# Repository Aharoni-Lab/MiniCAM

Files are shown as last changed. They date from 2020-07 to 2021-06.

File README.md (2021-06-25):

# MiniCAM
The MiniCAM is an open-source behaviroal camera for imaging freely behaving animals in behavioral and neuroscience experiments. The goal of the MiniCAM project is to provide an open-source, customizable, high-quality, and affordable alternative to using webcams or scientific USB cameras for behavioral imaging. The MiniCAM is powered and communicates over any commercial 50ohm coaxial cable minimizing the cabling that needs to run into the experimental environment. The coaxial cable connects the MiniDAQ to any version of UCLA Miniscope DAQs or MiniDAQs which then connects over USB3 to a host computer.

Using the [Miniscope Software](https://github.com/Aharoni-Lab/Miniscope-DAQ-QT-Software), multiple Miniscopes and MiniCAMs can be connected, streamed, and time-sync'ed recording simultaniously.

<p align="center">
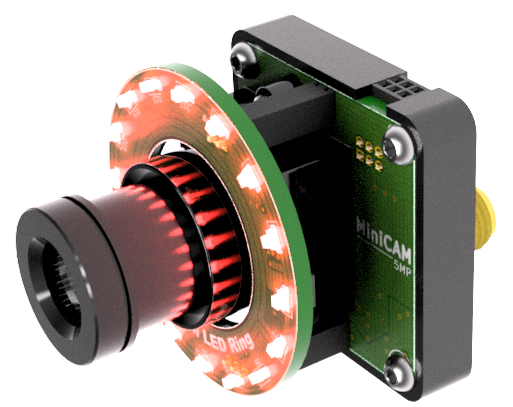
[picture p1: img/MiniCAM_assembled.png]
  
</p>

## MiniCAM Components
The MiniCAM consists of a custom printed circuit board (PCB), a 3D printed housing, an off the shelf M12 lens mount, a M12 camera lens, and an optional LED illumination ring. The PCB contains a 5MP CMOS image sensor, support electronics to power and serialize the imaging data, and an SMA coax connector. The image sensor can be configured through the Miniscope software and the optional LED illumination ring intensity can also be controlled through software. The MiniCAM runs at 50fps with 1024X768 resolution as the default configuration. Higher frame rate can be achieved by choosing smaller resolutions and higher resolution comes with lower frame rate.

<p align="center">
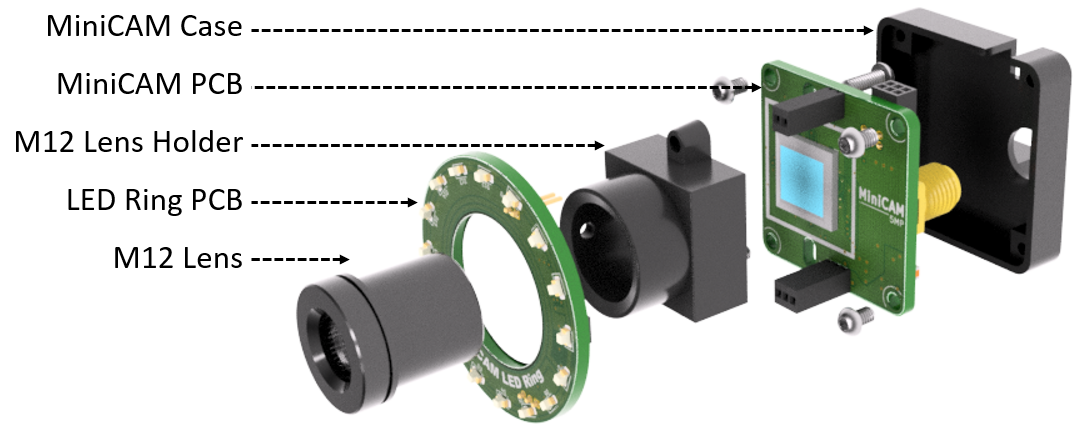
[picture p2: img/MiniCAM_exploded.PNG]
  
</p>

## System Layout
The MiniCAM requires a UCLA Miniscope Data Acquisition (DAQ) board (connected over a 50ohm coaxial cable) and a host computer (connected over USB3) running the [Miniscope Software](https://github.com/Aharoni-Lab/Miniscope-DAQ-QT-Software) (or other third-party application that can stream UVC cameras and can communicate through a Miniscope DAQ). You can use any generation of Miniscope DAQ but you must update it with [the newest firmware](https://github.com/Aharoni-Lab/Miniscope-DAQ-Cypress-firmware). You can also use the cheaper and smaller version of the Miniscope DAQ called the MiniDAQ (open-source link coming soon). Once updated to the newest firmware, any Miniscope DAQ device will work with all Miniscope and MiniCAM devices. 

<p align="center">
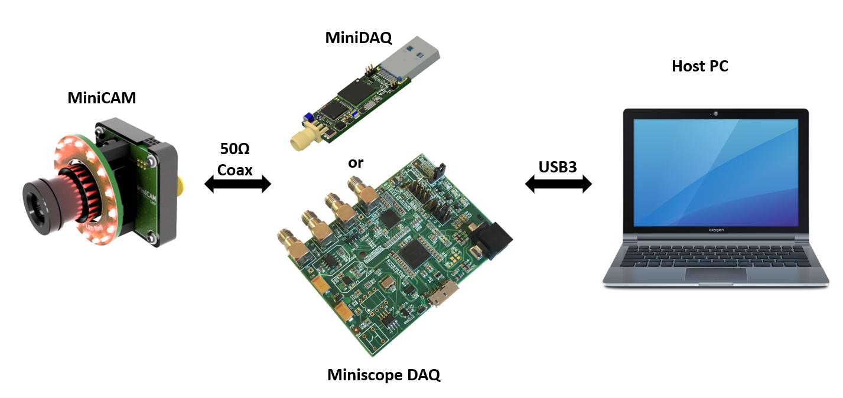
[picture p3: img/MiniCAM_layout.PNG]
  
</p>

## M12 lenses and Coaxial Cables
Just like Miniscopes, the MiniCAM uses a 50Ohm coaxial cable for power, communication, and data. Any 50Ohm coax cable should work with the system. 

### M12 lenses
M12 lenses and M12 Mount Lens Holders are avaiable in Amazon (can be purchased at other places too). It can be handy to buy a M12 Lens Kit that comes with a range of M12 lenses for different view angles. We have been happy with the Arducam lens set which can be found on Amazon. If you are using the optional LED illumination ring or other nIR light source make sure to remove any IR filter located in the lens if applicable.

### Coaxial Cables
Any 50Ohm coaxial cable should be compatible with this system. It is not necessary to use the expensive, thin, flexible coax cables generally used with Miniscopes. The thicker the cable the longer length you can run (maxing out at around 10 to 15 meters). It generally is most convinient to get a coax cable with male SMA connectors on both ends to connect between the MiniCAM and MiniDAQ (or standard Miniscope DAQ).

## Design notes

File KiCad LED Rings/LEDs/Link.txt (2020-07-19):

https://www.soselectronic.com/standard-leds?query=kptd&params=9%3ARed%7C121%3A30&param_current=121

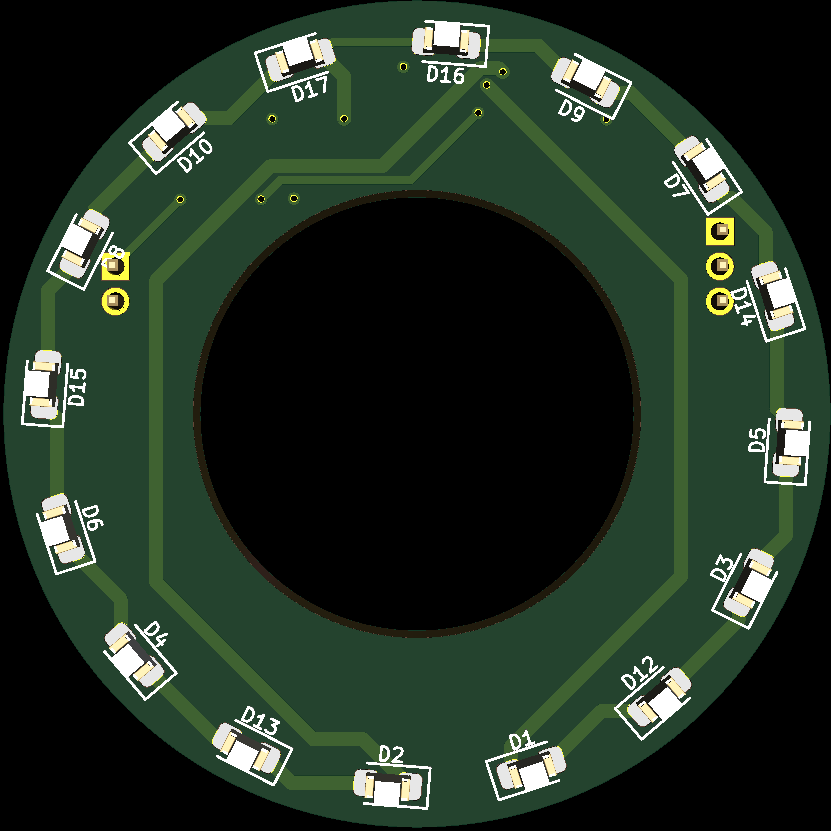
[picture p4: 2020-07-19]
KiCad LED Rings/LED Rings-V2 Skins/Front.PNG

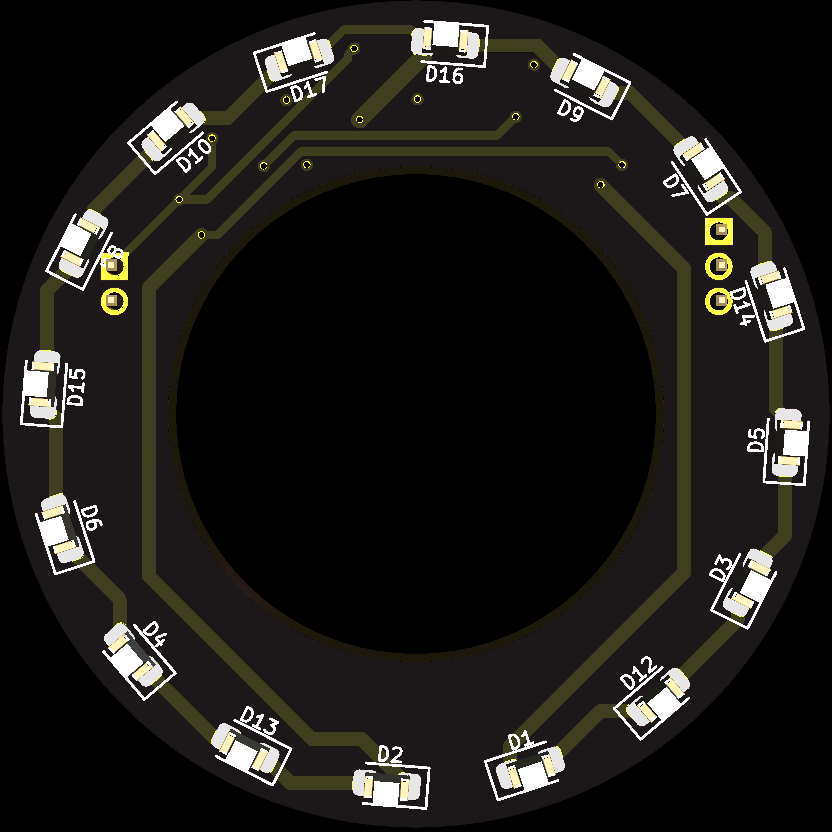
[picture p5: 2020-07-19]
KiCad LED Rings/LED Rings-V2 Skins/Front_b.png

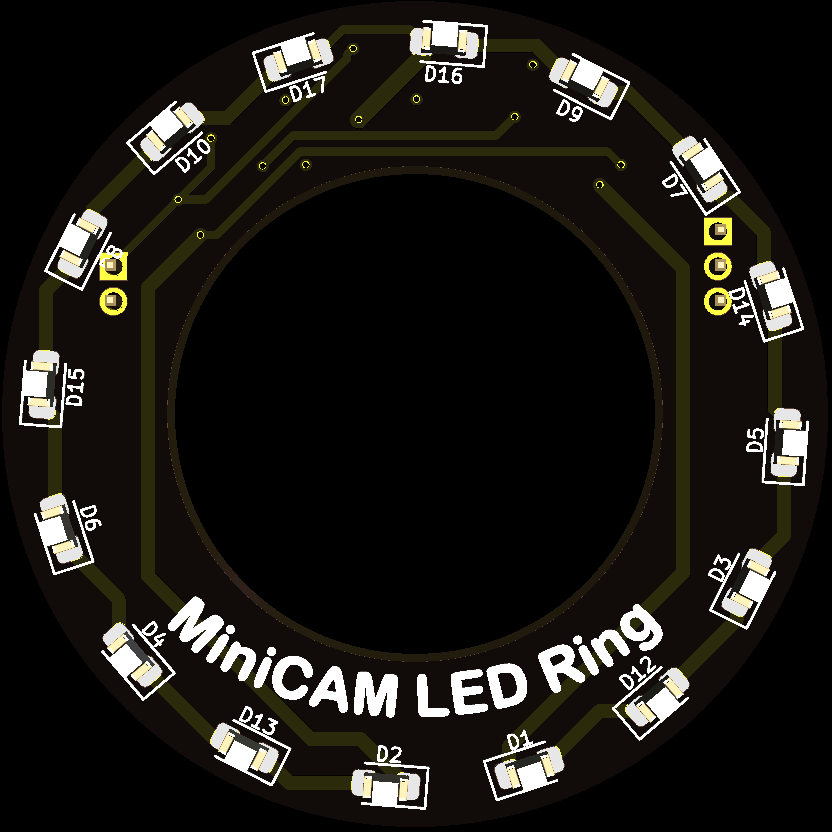
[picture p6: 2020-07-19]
KiCad LED Rings/LED Rings-V2 Skins/Front_b2.png

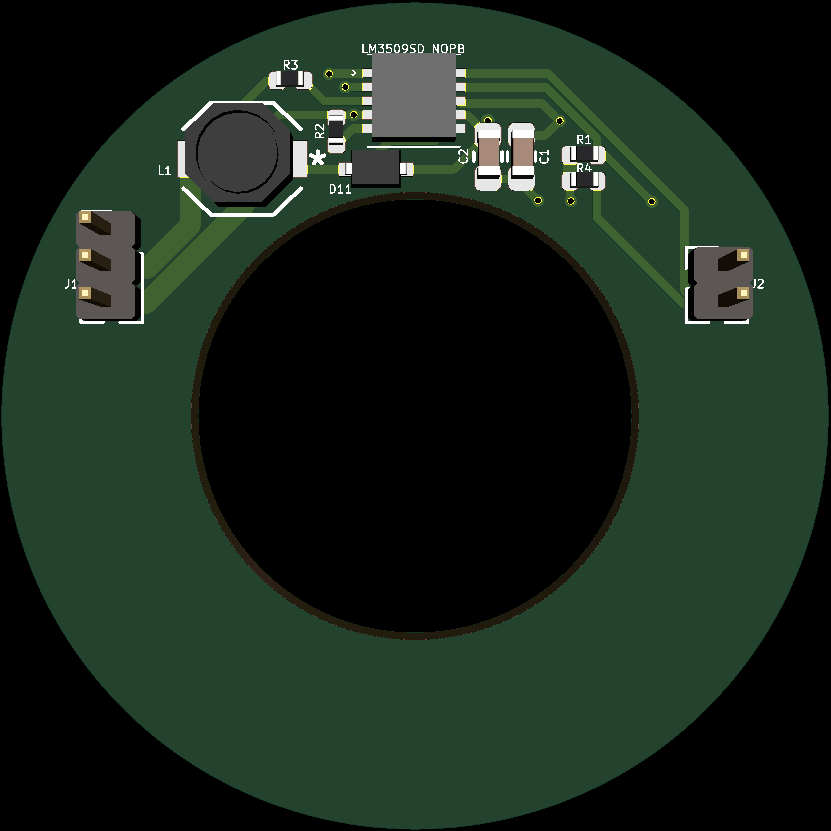
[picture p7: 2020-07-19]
KiCad LED Rings/LED Rings-V2 Skins/Back.PNG

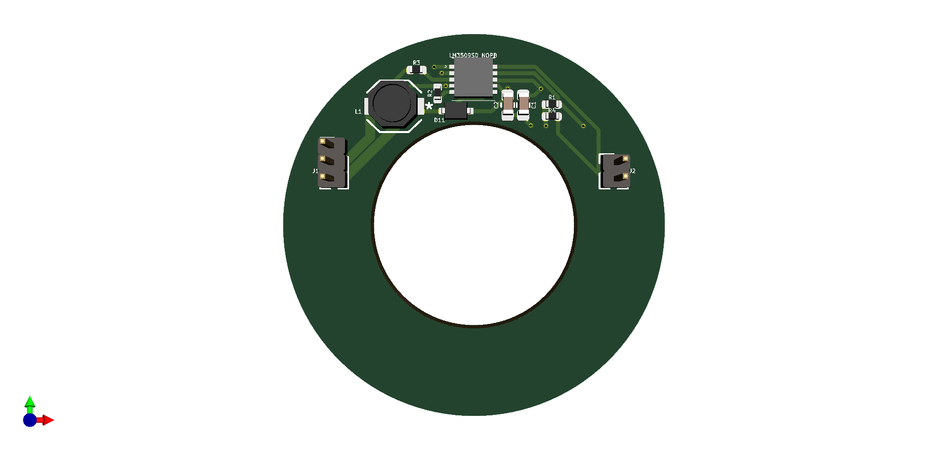
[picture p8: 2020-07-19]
KiCad LED Rings/LED Rings-V2 Skins/Kicad_BehaviorCamera_V2 v5_B.png

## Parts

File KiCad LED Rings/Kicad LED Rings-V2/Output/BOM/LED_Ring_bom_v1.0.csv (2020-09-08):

Component | Description | Part | References | Value | Footprint | Quantity Per PCB | Datasheet | PartNo.
1 |  | GRM033R60J105MEA2D-.Capacitor-Kicad-LED-Rings-rescue-Kicad-LED-Rings-rescue | C1 | 1uF | C_0603_1608Metric_L | 1 | ~ | GRT188R61C105KE13D
2 |  | GRM033R60J105MEA2D-.Capacitor-Kicad-LED-Rings-rescue-Kicad-LED-Rings-rescue | C2 | 2.2uF | C_0805_2012Metric_L | 1 | https://www.digikey.com/product-detail/en/tdk-corporation/C2012X5R1E225M125AC/445-7630-2-ND/2733065 | C2012X5R1E225M125AC
3 |  | BAT760,115-BAT760_115-Kicad-LED-Rings-rescue | D17 | D_Schottky | SOD323(F) | 1 | https://www.digikey.com/product-detail/en/nexperia-usa-inc/BAT760115/1727-4825-1-ND/2531312 | BAT760,115
4 |  | LED_Small_ALT-Device-Kicad-LED-Rings-rescue | D1 D2 D3 D4 D5 D6 D7 D8 D9 D10 D11 D12 D13 D14 D15 D16 | LED_Small_ALT | LED_0603_1608Metric | 16 | https://www.digikey.com/product-detail/en/lite-on-inc/LTST-C190KRKT/160-1436-1-ND/386816 | LTST-C190KRKT
5 |  | Conn_01x03_Female-Connector-Kicad-LED-Rings-rescue | J1 | Conn_01x02_Female | PinHeader_1x03_P1.27mm_Vertical | 1 | ~
6 |  | Conn_01x02_Male-Connector-Kicad-LED-Rings-rescue | J2 | Conn_01x02_Male | PinHeader_1x02_P1.27mm_Vertical | 1 | ~
7 |  | NRS4012T100MDGJ-2020-07-30_23-38-29 | L1 | 10uH | NR3015T1R5N | 1 | https://www.digikey.com/product-detail/en/taiyo-yuden/NRS4012T100MDGJ/587-2878-1-ND/2648998 | NRS4012T100MDGJ
8 |  | R_Small-Device-Kicad-LED-Rings-rescue | R1 R4 | 3K | R_0402_1005Metric_ERJ_L | 2 | https://www.digikey.in/product-detail/en/panasonic-electronic-components/ERA-2AEB302X/P3-0KDCTR-ND/1706016 | ERA-2AEB302X
9 |  | R_Small-Device-Kicad-LED-Rings-rescue | R2 R3 | 9.5k | R_0402_1005Metric_ERJ_L | 2 | https://www.digikey.com/product-detail/en/panasonic-electronic-components/ERA-2AEB123X/P12KDCCT-ND/1706209 | ERA-2AEB9531X
10 |  | LM3509SD_NOPB-2020-04-05_20-57-04-Kicad-LED-Rings-rescue | U1 | LM3509SD_NOPB | LM3509SDNOPB | 1 |  | LM3509SD_NOPB
Component Groups: | 10
Component Count: | 27
Fitted Components: | 27
Number of PCBs: | 1
Total components: | 27
Schematic Version: | v1.0
Schematic Date: | 2020-09-08
PCB Variant: | [u'default']
BoM Date: | 9/8/2020 11:45:49 AM
Schematic Source: | LED_Ring.sch
KiCad Version: | Eeschema (5.1.6)-1

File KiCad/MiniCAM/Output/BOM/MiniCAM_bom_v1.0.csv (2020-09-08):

Component | Description | Part | References | Value | Footprint | Quantity Per PCB | Datasheet | Part Number | Note | Size
1 | Unpolarized capacitor, small symbol | C_Small | C18 C21 C26 C29 C31 C34 | 10nF | C_0402_1005Metric_L | 6 | ~ | GCM155R71E103KA37D
2 | Unpolarized capacitor, small symbol | C_Small | C25 | 47nF | C_0402_1005Metric_L | 1 | ~ | GRM155R71A473KA01D
3 | Unpolarized capacitor, small symbol | C_Small | C4 C5 C6 C7 C8 C9 C10 C14 C15 C19 C22 C24 C27 C30 C32 | 0.1uF | C_0402_1005Metric_L | 15 | ~ | GCM155R71C104KA55J
4 | Unpolarized capacitor, small symbol | C_Small | C1 C2 C3 C11 C16 C33 C35 | 1uF | C_0402_1005Metric_L | 7 | ~ | GRT155R61C105KE01D
5 | Unpolarized capacitor, small symbol | C_Small | C20 C23 C28 | 4.7uF | C_0402_1005Metric_L | 3 | ~ | CC0402MRX5R6BB475
6 | Unpolarized capacitor, small symbol | C_Small | C12 C13 C17 C36 | 10uF | C_0603_1608Metric_L | 4 | ~ | GRM188R61A106KE69J
7 | Light emitting diode, small symbol, filled shape | LED_Small_ALT | D1 | LED_Small_ALT | LED_SC80X160X65L40L | 1 | ~ | LTST-C190KRKT
8 | Generic connector, single row, 01x02, script generated (kicad-library-utils/schlib/autogen/connector/) | Conn_01x02 | J2 | Conn_01x02 | PinSocket_1x02_P1.27mm_Vertical | 1 | ~ | DNL
9 | Generic connector, single row, 01x03, script generated (kicad-library-utils/schlib/autogen/connector/) | Conn_01x03 | J3 | Conn_01x03 | PinSocket_1x03_P1.27mm_Vertical | 1 | ~ | DNL
10 | Generic connector, double row, 02x03, odd/even pin numbering scheme (row 1 odd numbers, row 2 even numbers), script generated (kicad-library-utils/schlib/autogen/connector/) | Conn_02x03_Odd_Even | J4 | Conn_02x03_Odd_Even | PinSocket_2x03_P1.27mm_Horizontal | 1 | ~ | DNL
11 | CONN SMA JACK R/A 50 OHM PCB | SMA-J-P-H-RA-TH1 | J1 | SMA-J-P-H-RA-TH1 | SMA_Amphenol_132134-10_Vertical | 1 | http://suddendocs.samtec.com/catalog_english/sma.pdf | CONSMA001-SMD-G-T
12 | FIXED IND 47UH 500MA 900 MOHM | ADL3225V-470MT-TL000 | L2 | ADL3225V-470MT-TL000 | L_1210_3225Metric_L | 1 | https://product.tdk.com/info/en/catalog/datasheets/inductor_automotive_decoupling_adl3225v_en.pdf | ADL3225V-470MT-TL000 | 47uH | 1210
13 | FERRITE BEAD 470 OHM 0603 1LN | BLM18PG471SN1D | L1 L3 L4 L5 | BLM18PG471SN1D | L_0603_1608Metric_L | 4 | https://www.murata.com/en-us/products/productdata/8796738650142/ENFA0003.pdf | BLM18PG471SN1D | 470 Ohms @ 100MHz | 0603
14 | Resistor, small US symbol | R_Small_US | R11 R12 R13 | 0 | R_0402_1005Metric_ERJ_L | 3 | ~ | ERJ-2GE0R00X
15 | Resistor, small US symbol | R_Small_US | R3 | 50 | R_0402_1005Metric_ERJ_L | 1 | ~ | ERJ-2RKF49R9X
16 | Resistor, small US symbol | R_Small_US | R4 | 1K | R_0402_1005Metric_ERJ_L | 1 | ~ | ERJ-2GEJ102X
17 | Resistor, small US symbol | R_Small_US | R1 R2 R5 R6 | 2K | R_0402_1005Metric_ERJ_L | 4 | ~ | ERJ-2RKF2001X
18 | Resistor, small US symbol | R_Small_US | R7 R8 | 10K | R_0402_1005Metric_ERJ_L | 2 | ~ | ERJ-2RKF1002X
19 | Resistor, small US symbol | R_Small_US | R9 | 100K | R_0402_1005Metric_ERJ_L | 1 | ~ | ERJ-2RKF1003X
20 | IC SERIALIZER FPD-LINK 32WQFN | DS90UB933-Q1 | U2 | DS90UB933-Q1 | QFN_33_P50_500X500X80L40X24T310L | 1 | http://www.ti.com/lit/ds/symlink/ds90ub933-q1.pdf | DS90UB913ATRTVTQ1
21 |  | MT9P031 | U3 | MT9P031 | iLCC48P70_1000X1000X135L80X40N | 1 | https://www.onsemi.com/pub/Collateral/MT9P031-D.PDF | MT9P031I12STM
22 | Voltage Regulator - Dual 300mA fixed | NCV8154 | U1 | NCV8154MW180280TBG | DFN10_3x3_11P50_300X300X100L40X24T250X180N | 1 | https://www.onsemi.com/pub/Collateral/NCV8154-D.PDF | NCV8154MW180280TBG
23 | MEMS OSC XO | SiT_2.5mmx2mm | U4 | SiT_2.5mmx2mm | OSC_CC250X200X80L70X75L | 1 | https://www.sitime.com/datasheet/SiT8008 | DSC1001DI2-096.0000
Component Groups: | 24
Component Count: | 63
Fitted Components: | 62
Number of PCBs: | 1
Total components: | 62
Schematic Version: | v1.0
Schematic Date: | 2020-09-01
PCB Variant: | [u'default']
BoM Date: | 9/8/2020 11:32:33 AM
Schematic Source: | MiniCAM.sch
KiCad Version: | Eeschema (5.1.6)-1

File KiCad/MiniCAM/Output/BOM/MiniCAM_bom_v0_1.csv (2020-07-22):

Component | Description | Part | References | Value | Footprint | Quantity Per PCB | Datasheet | Part Number | Note | Size | LCSC Part #
1 | Unpolarized capacitor, small symbol | C_Small | C4 C5 C6 C7 C8 C9 C10 C14 C15 C19 C22 C24 C27 C30 C32 | 0.1uF | C_0402_1005Metric_L | 15 | ~ | GCM155R71C104KA55J
2 | Unpolarized capacitor, small symbol | C_Small | C18 C21 C26 C29 C31 C34 | 10nF | C_0402_1005Metric_L | 6 | ~ | GCM155R71E103KA37D
3 | Unpolarized capacitor, small symbol | C_Small | C12 C13 C17 C36 | 10uF | C_0603_1608Metric_L | 4 | ~ | GRM188R61A106KE69J
4 | Unpolarized capacitor, small symbol | C_Small | C1 C2 C3 C11 C16 C33 C35 | 1uF | C_0402_1005Metric_L | 7 | ~ | GRT155R61C105KE01D |  |  | C363938
5 | Unpolarized capacitor, small symbol | C_Small | C20 C23 C28 | 4.7uF | C_0402_1005Metric_L | 3 | ~ | CC0402MRX5R6BB475
6 | Unpolarized capacitor, small symbol | C_Small | C25 | 47nF | C_0402_1005Metric_L | 1 | ~ | GRM155R71A473KA01D
7 | Light emitting diode, small symbol, filled shape | LED_Small_ALT | D1 | LED_Small_ALT | LED_SC80X160X65L40L | 1 | ~ | LTST-C190KRKT |  |  | C2286
11 | CONN SMA JACK R/A 50 OHM PCB | SMA-J-P-H-RA-TH1 | J1 | SMA-J-P-H-RA-TH1 | SMA_Amphenol_132134-10_Vertical | 1 | http://suddendocs.samtec.com/catalog_english/sma.pdf | CONSMA001-SMD-G-T
12 | FIXED IND 47UH 500MA 900 MOHM | ADL3225V-470MT-TL000 | L2 | ADL3225V-470MT-TL000 | L_1210_3225Metric_L | 1 | https://product.tdk.com/info/en/catalog/datasheets/inductor_automotive_decoupling_adl3225v_en.pdf | ADL3225V-470MT-TL000 | 47uH | 1210 | C435260
13 | FERRITE BEAD 470 OHM 0603 1LN | BLM18PG471SN1D | L1 L3 L4 L5 | BLM18PG471SN1D | L_0603_1608Metric_L | 4 | https://www.murata.com/en-us/products/productdata/8796738650142/ENFA0003.pdf | BLM18PG471SN1D | 470 Ohms @ 100MHz | 603 | C97853
14 | Resistor, small US symbol | R_Small_US | R11 R12 R13 | 0 | R_0402_1005Metric_ERJ_L | 3 | ~ | ERJ-2GE0R00X
15 | Resistor, small US symbol | R_Small_US | R9 | 100K | R_0402_1005Metric_ERJ_L | 1 | ~ | ERJ-2RKF1003X
16 | Resistor, small US symbol | R_Small_US | R7 R8 | 10K | R_0402_1005Metric_ERJ_L | 2 | ~ | ERJ-2RKF1002X
17 | Resistor, small US symbol | R_Small_US | R4 | 1K | R_0402_1005Metric_ERJ_L | 1 | ~ | ERJ-2GEJ102X
18 | Resistor, small US symbol | R_Small_US | R1 R5 R6 | 2K | R_0402_1005Metric_ERJ_L | 3 | ~ | ERJ-2RKF2001X
19 | Resistor, small US symbol | R_Small_US | R3 | 50 | R_0402_1005Metric_ERJ_L | 1 | ~ | ERJ-2RKF49R9X |  |  | C441726
20 | Resistor, small US symbol | R_Small_US | R2 | 500 | R_0402_1005Metric_ERJ_L | 1 | ~ | ERJ-2RKF4990X |  |  | C137970
21 | IC SERIALIZER FPD-LINK 32WQFN | DS90UB933-Q1 | U2 | DS90UB933-Q1 | QFN_33_P50_500X500X80L40X24T310L | 1 | http://www.ti.com/lit/ds/symlink/ds90ub933-q1.pdf | DS90UB913ATRTVTQ1
23 | Voltage Regulator - Dual 300mA fixed | NCV8154 | U1 | NCV8154MW180280TBG | DFN10_3x3_11P50_300X300X100L40X24T250X180N | 1 | https://www.onsemi.com/pub/Collateral/NCV8154-D.PDF | NCV8154MW180280TBG
Component Groups: | 25
Component Count: | 63
Fitted Components: | 62
Number of PCBs: | 1
Total components: | 62
Schematic Version:
Schematic Date:
PCB Variant: | default
BoM Date: | 7/21/2020 23:12
Schematic Source: | C:\Users\DBAharoni\Documents\Projects\MiniCAM\KiCad\MiniCAM\MiniCAM.sch
KiCad Version: | Eeschema (5.1.5)-3

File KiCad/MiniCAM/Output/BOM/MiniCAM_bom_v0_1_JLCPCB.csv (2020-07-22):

Component | Comment | Designator | Footprint | LCSC Part #
1 | 0.1uF | C4 C5 C6 C7 C8 C9 C10 C14 C15 C19 C22 C24 C27 C30 C32 | 0402_C
2 | 10nF | C18 C21 C26 C29 C31 C34 | 0402_C
3 | 10uF | C12 C13 C17 C36 | 0402_C
4 | 1uF | C1 C2 C3 C11 C16 C33 C35 | 0402_C | C363938
5 | 4.7uF | C20 C23 C28 | 0402_C
6 | 47nF | C25 | 0402_C
7 | LED_Small_ALT | D1 | 0603_LED | C2286
11 | SMA-J-P-H-RA-TH1 | J1 | SMA_Amphenol_132134-10_Vertical
12 | ADL3225V-470MT-TL000 | L2 | 1210_L | C435260
13 | BLM18PG471SN1D | L1 L3 L4 L5 | 0603_L | C97853
14 | 0 | R11 R12 R13 | 0402_R
15 | 100K | R9 | 0402_R
16 | 10K | R7 R8 | 0402_R
17 | 1K | R4 | 0402_R
18 | 2K | R1 R5 R6 | 0402_R
19 | 50 | R3 | 0402_R | C441726
20 | 500 | R2 | 0402_R | C137970
21 | DS90UB933-Q1 | U2 | QFN_33_P50_500X500X80L40X24T310L
23 | NCV8154MW180280TBG | U1 | DFN10_3x3_11P50_300X300X100L40X24T250X180N
Component Groups:
Component Count:
Fitted Components:
Number of PCBs:
Total components:
Schematic Version:
Schematic Date:
PCB Variant:
BoM Date:
Schematic Source:
KiCad Version:

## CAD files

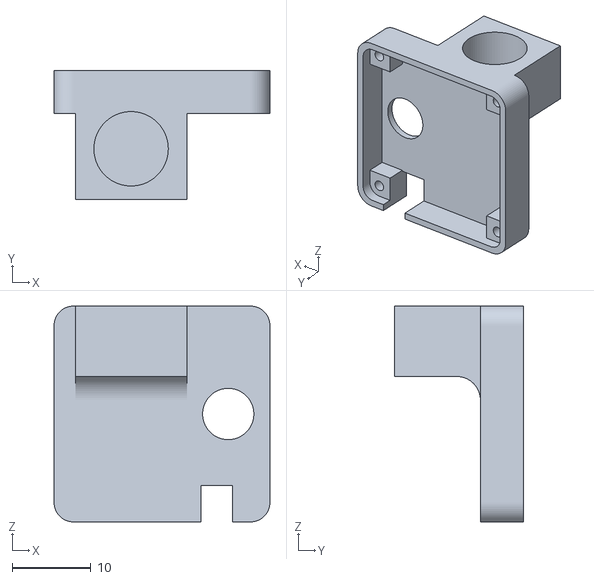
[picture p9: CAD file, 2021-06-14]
Housing/MiniCAM_5MP_Back_Housing.stl
27.4 x 16.4 x 27.4

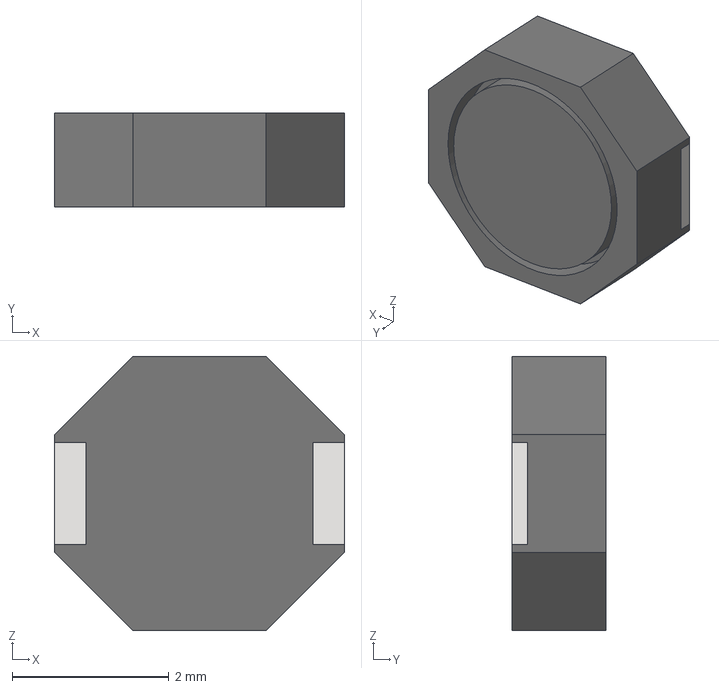
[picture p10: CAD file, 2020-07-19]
KiCad LED Rings/10uH Inductor/10uH Inductor_VLF4012AT-100MR79 v2.step
3.70 x 1.20 x 3.50 mm

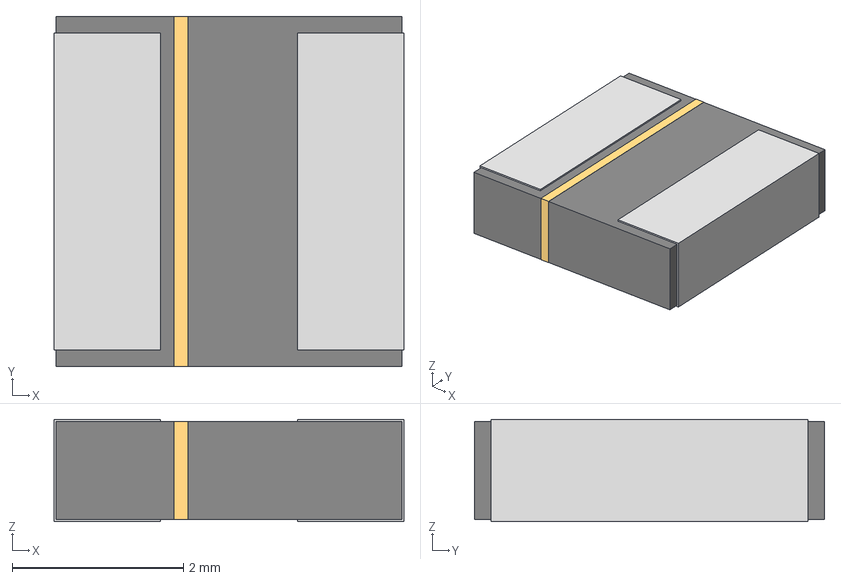
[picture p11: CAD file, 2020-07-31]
KiCad LED Rings/10uH Inductor/NRS4012T100MDGJ/ul_NRS4012T100MDGJ/STEP/IND_TAIYO_NRS4012_TAY.step
4.09 x 4.09 x 1.19 mm

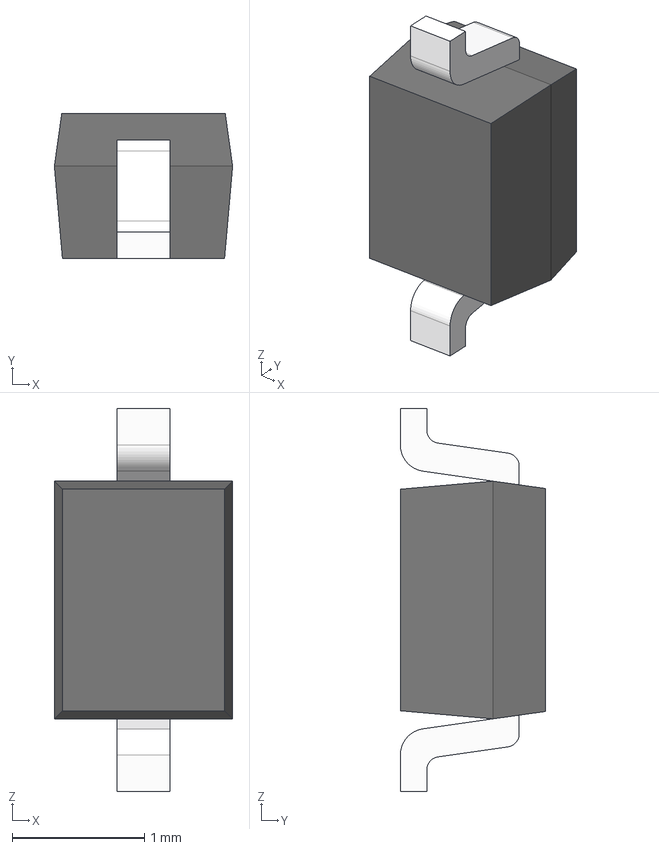
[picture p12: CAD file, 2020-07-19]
KiCad LED Rings/Diode Schottky/Diode-Schottky-BAT760 v5.step
1.35 x 1.10 x 2.90 mm

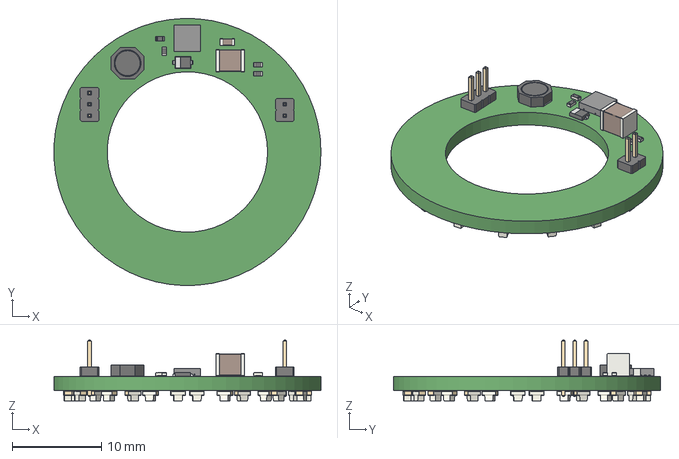
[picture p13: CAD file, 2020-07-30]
KiCad LED Rings/Kicad LED Rings-V2/Kicad LED Rings.step
30.0 x 30.0 x 6.80 mm

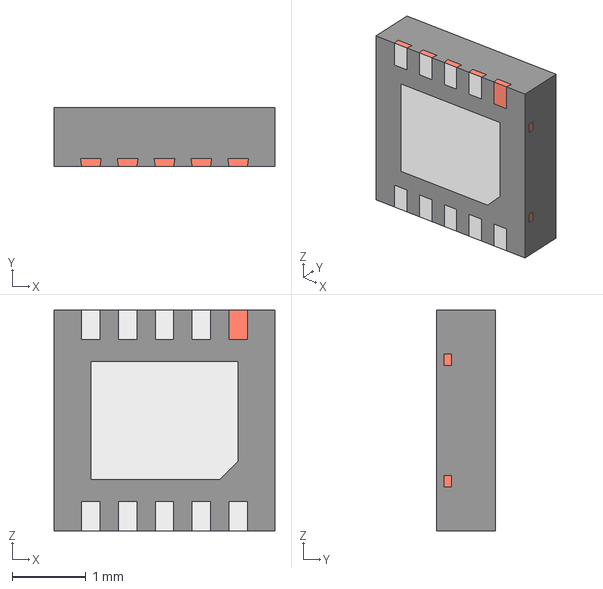
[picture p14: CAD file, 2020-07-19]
KiCad LED Rings/LED Drivers/ul_LM3509SDNOPB/STEP/DSC0010A.stp
3.00 x 0.8 x 3.00 mm
BODY_SDA10A
FRAME_SDA10A

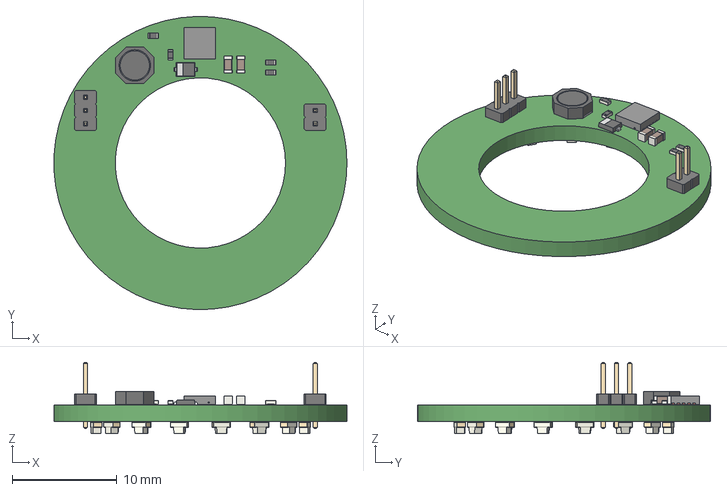
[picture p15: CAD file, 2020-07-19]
KiCad LED Rings/Kicad LED Rings-V2/Kicad LED Rings_Circular_final.step
28.0 x 28.0 x 6.80 mm

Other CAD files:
KiCad LED Rings/Kicad LED Rings-V2/Kicad LED Rings_Circular_final_V2.step

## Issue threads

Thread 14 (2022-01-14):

### ISSUE TITLE
Triggering, IR filters

### ISSUE THREAD

**Issue by generalciao** [Aharoni-Lab/MiniCAM#14]
Can MiniCam be triggered by an external TTL source, so that frames are synchronized to e.g. a 2P microscope system? Along those lines, which wavelength does the IR ring use, and is it possible/easy to obtain and attach IR filters in front of the lens (for example to block ~920 nm IR light from intracranial 2P imaging)? Curious about using the MiniCam in place of more expensive options for simple pupil, whisker, paw, etc. tracking (DeeplabCut) on a 2P setup. Thanks :)

**Comment by daharoni** [comment]
Unfortunately the MiniCAM cannot currently be externally trigged on a frame by frame basis. That said, if using the Miniscope DAQ PCB and Software, you can enable external TTL triggering to start and stop recording sessions (but doesn't trigger individual frames).

The MiniCAM itself does not have any IR filtering as part of the image sensor or PCB. Any filtering you might want to do can be done by placing a thin filter right on top of the image sensor or by using M12 lenses that incorporate a filter in them.

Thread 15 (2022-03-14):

### ISSUE TITLE
spectral sensitivity and quantum efficiency

### ISSUE THREAD

**Issue by MariangelaP** [Aharoni-Lab/MiniCAM#15]
Hello, I'd be interested in using your miniCAM to monitor head-fixed behaviour in an operant box. Frame rate and resolution seem to be appropriate for my experiments. I just have a couple of extra questions for you. 
1) what are the dimensions of the MiniCAM?
2) what's the spectral sensitivity?
3) what's the quantum efficiency?

thank you!

**Comment by daharoni** [comment]
Hello.
1. The MiniCAM is ~25mm x 25mm and has a 1/4" - 20 threaded insert for mounting.
2. Unfortunately we do not have this information as it isn't provided in the CMOS image sensors data sheet and we haven't measured it directly ourselves. That said, it definitely has decent sensitivity up to NIR as long as you do not use an M12 lens with an IR fitler.
3. Unfortunately we do not have this information as it isn't provided in the CMOS image sensors data sheet and we haven't measured it directly ourselves.

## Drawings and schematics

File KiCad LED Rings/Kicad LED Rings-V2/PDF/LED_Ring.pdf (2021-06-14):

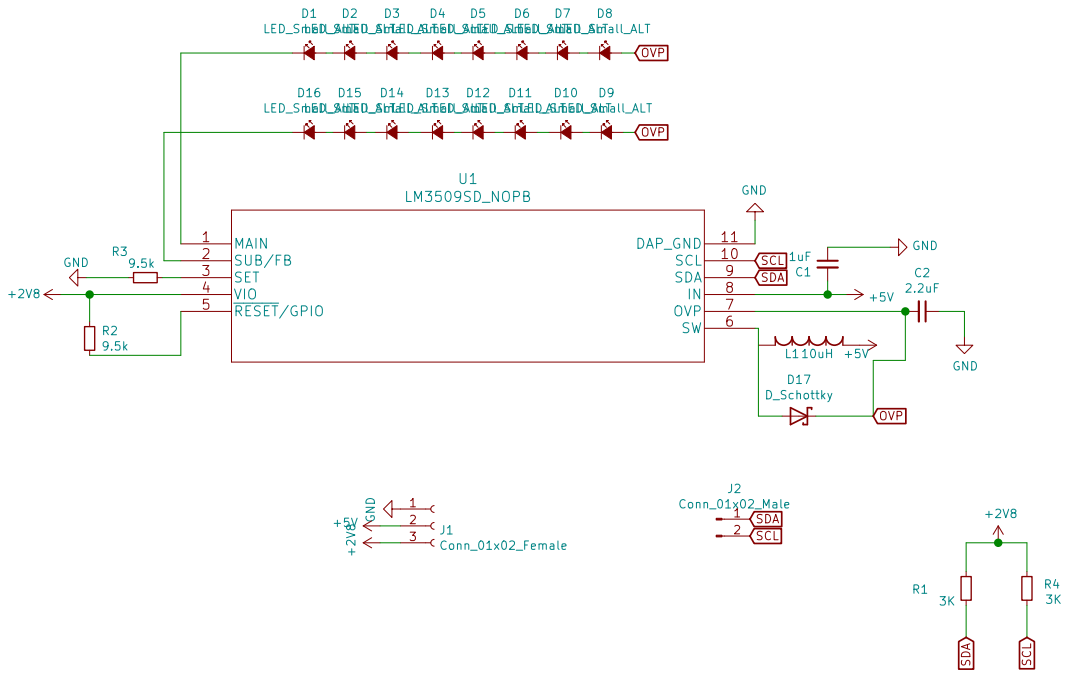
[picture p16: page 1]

File: LED_Ring.sch Sheet: / Aharoni Lab GND

Id: 1/1 Title: MiniCAM LED Ring

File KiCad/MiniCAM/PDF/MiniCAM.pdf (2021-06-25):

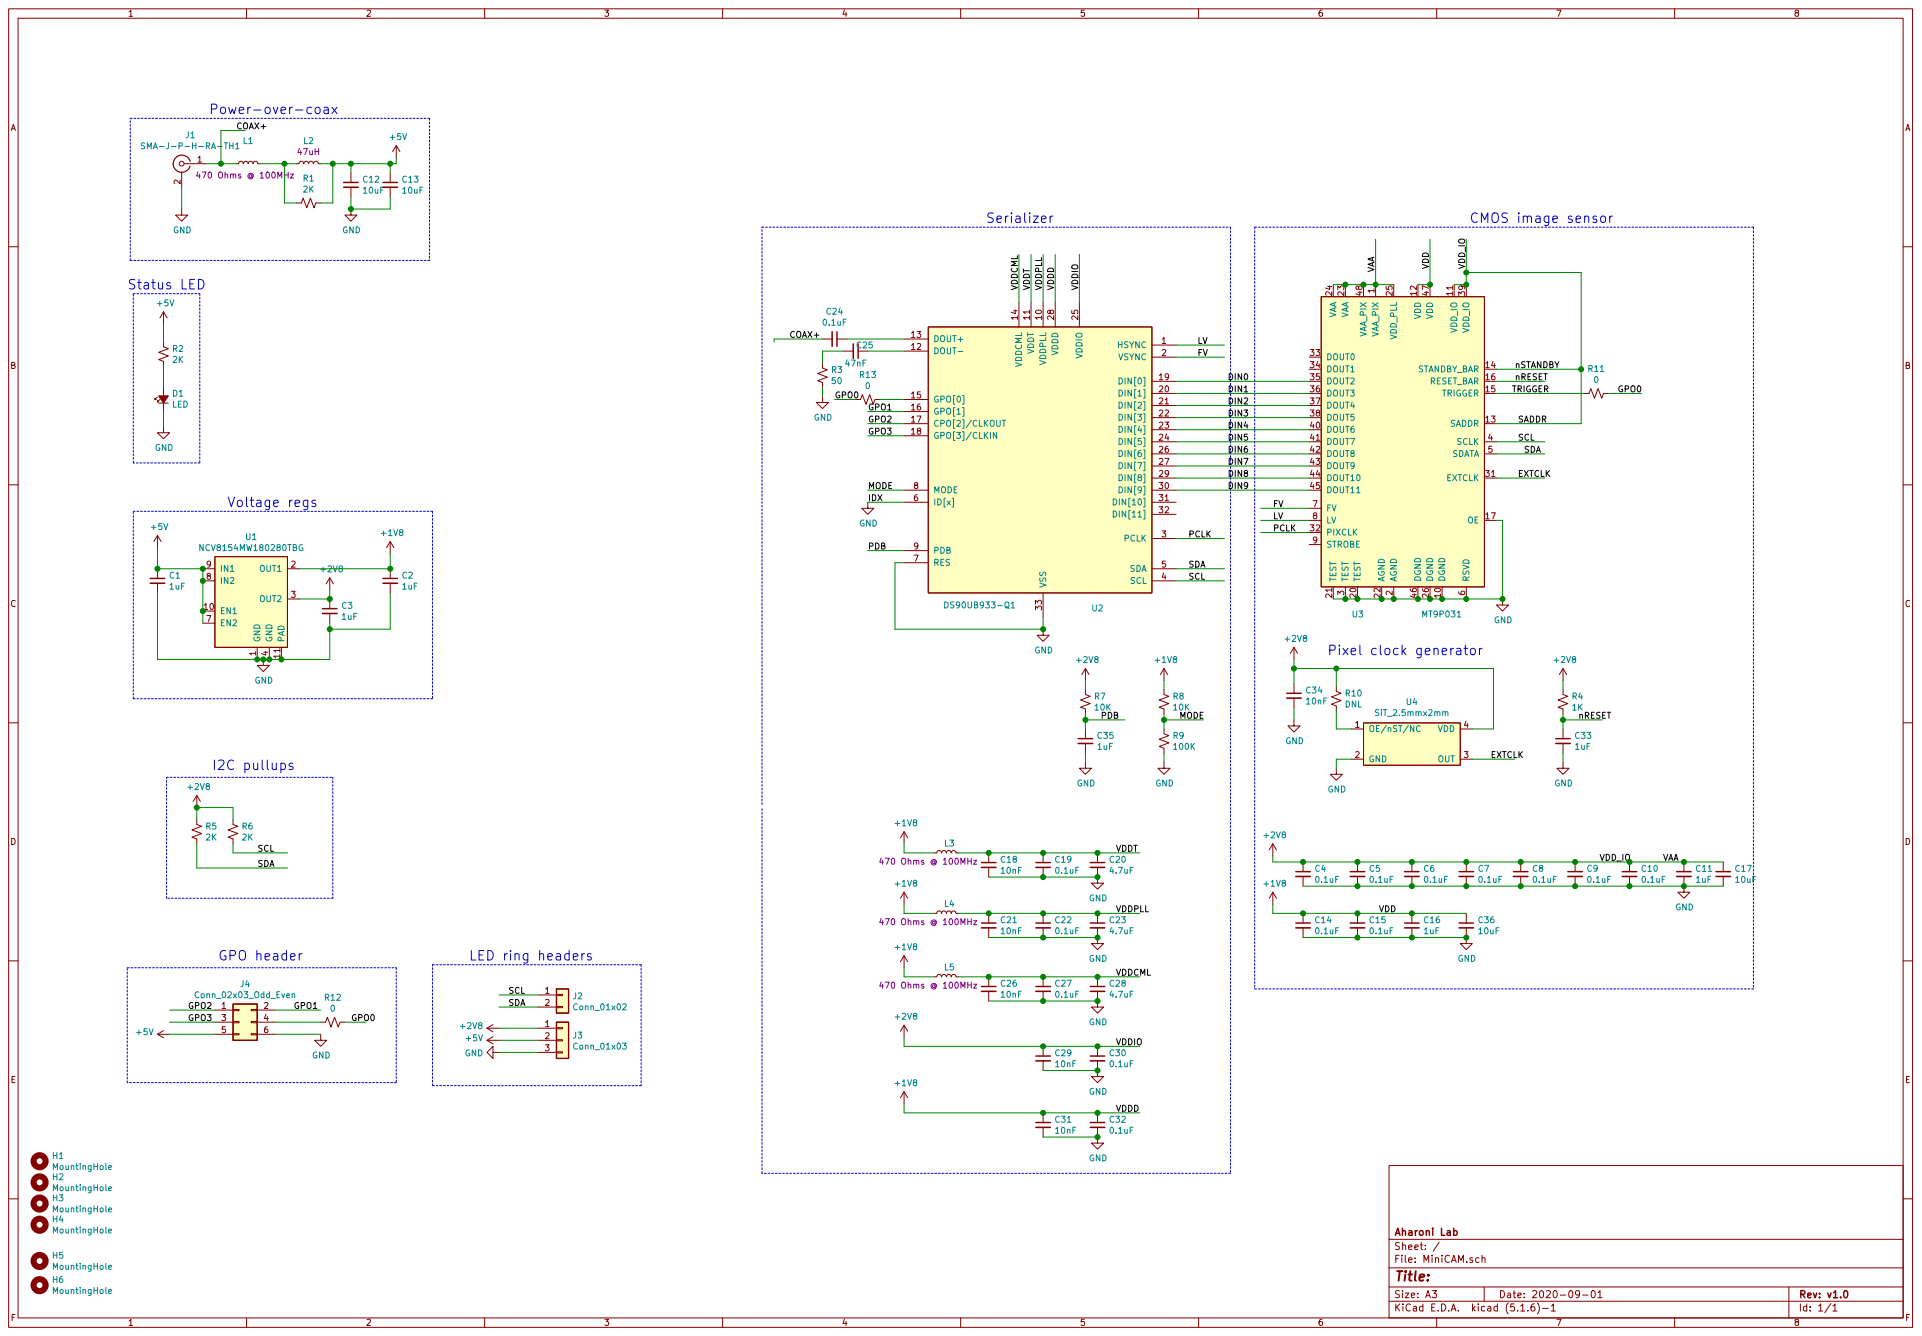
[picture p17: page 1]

3 EXTCLK 31 PIXCLK 32 DOUT0 33 DOUT1 34 DOUT2 35 DOUT3 36 DOUT4 37 DOUT5 38 VDD_IO 39 SCLK 4 DOUT6 40 DOUT7 41 DOUT8 42 DOUT9 43 DOUT10 44 DOUT11 45 DGND 46 VDD 47 VAA_PIX 48 SDATA 5 RSVD

2 TEST 20 TEST 21 AGND 22 VAA 23 VAA 24 VDD_PLL 25 DGND 26 TEST

1 DGND 10 VDD_IO 11 VDD 12 SADDR 13 STANDBY_BAR 14 TRIGGER 15 RESET_BAR 16 OE 17 AGND

Id: 1/1 Title: File: MiniCAM.sch Sheet: / Aharoni Lab

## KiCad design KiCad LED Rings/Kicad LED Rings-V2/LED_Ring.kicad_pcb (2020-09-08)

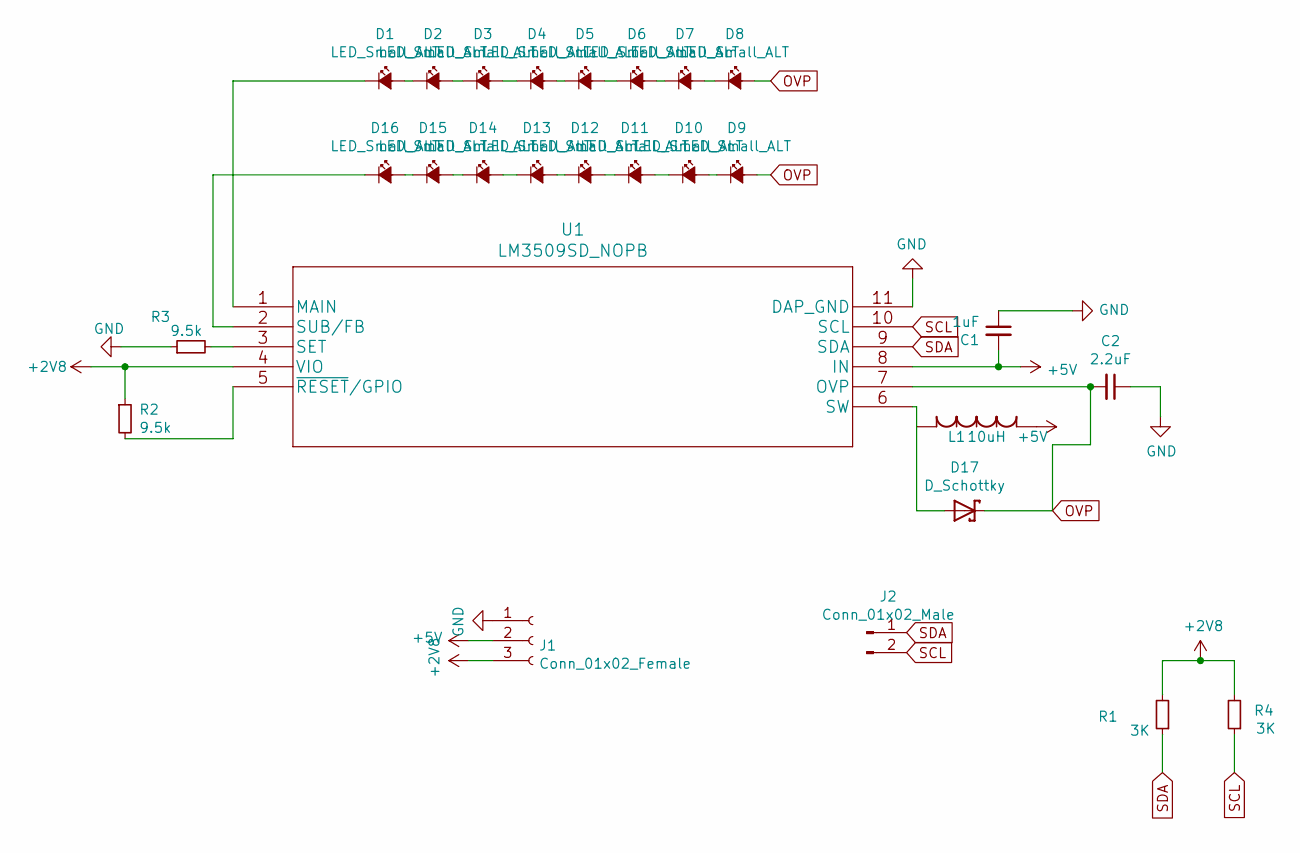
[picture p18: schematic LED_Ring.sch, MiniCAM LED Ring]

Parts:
C1: 1uF; C_0603_1608Metric_L; PartNo. GRT155C80J105ME01D
C2: 2.2uF; C_0805_2012Metric_L; PartNo. C2012X5R1E225M125AC
D1, D2, D3, D4, D5, D6, D7, D8, D9, D10, D11, D12, D13, D14, D15, D16: LED_Small_ALT; LED_0603_1608Metric; PartNo. LTST-C190KRKT
D17: D_Schottky; SOD323(F); PartNo. BAT760,115
J1: Conn_01x02_Female; PinHeader_1x03_P1.27mm_Vertical
J2: Conn_01x02_Male; PinHeader_1x02_P1.27mm_Vertical
L1: 10uH; NR3015T1R5N; PartNo. NRS4012T100MDGJ
R1, R4: 3K; R_0402_1005Metric_ERJ_L; PartNo. ERA-2AEB302X
R2, R3: 9.5k; R_0402_1005Metric_ERJ_L; PartNo. ERA-2AEB9531X
U1: LM3509SD_NOPB; LM3509SDNOPB; PartNo. LM3509SD_NOPB

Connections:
+2V8: J1.3, R1.2, R2.1, R4.2, U1.4 (VIO)
+5V: C1.2, J1.2, L1.1, U1.8 (IN)
GND: C1.1, C2.1, J1.1, R3.1, U1.11 (DAP_GND)
unnamed: D1.1 (K), U1.1 (MAIN)
unnamed: D1.2 (A), D2.1 (K)
unnamed: D2.2 (A), D3.1 (K)
unnamed: D3.2 (A), D4.1 (K)
unnamed: D4.2 (A), D5.1 (K)
unnamed: D5.2 (A), D6.1 (K)
unnamed: D6.2 (A), D7.1 (K)
unnamed: D7.2 (A), D8.1 (K)
unnamed: D10.1 (K), D11.2 (A)
unnamed: D9.1 (K), D10.2 (A)
unnamed: D11.1 (K), D12.2 (A)
unnamed: D12.1 (K), D13.2 (A)
unnamed: D13.1 (K), D14.2 (A)
unnamed: D14.1 (K), D15.2 (A)
unnamed: D15.1 (K), D16.2 (A)
unnamed: D16.1 (K), U1.2 (SUB/FB)
unnamed: R2.2, U1.5 (~RESET~/GPIO)
unnamed: R3.2, U1.3 (SET)
OVP: C2.2, D8.2 (A), D9.2 (A), D17.1 (K), U1.7 (OVP)
SCL: J2.2, R4.1, U1.10 (SCL)
SDA: J2.1, R1.1, U1.9 (SDA)

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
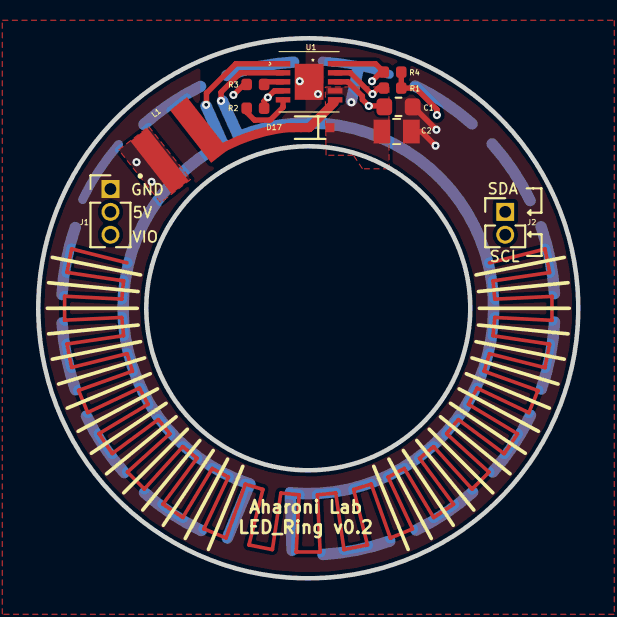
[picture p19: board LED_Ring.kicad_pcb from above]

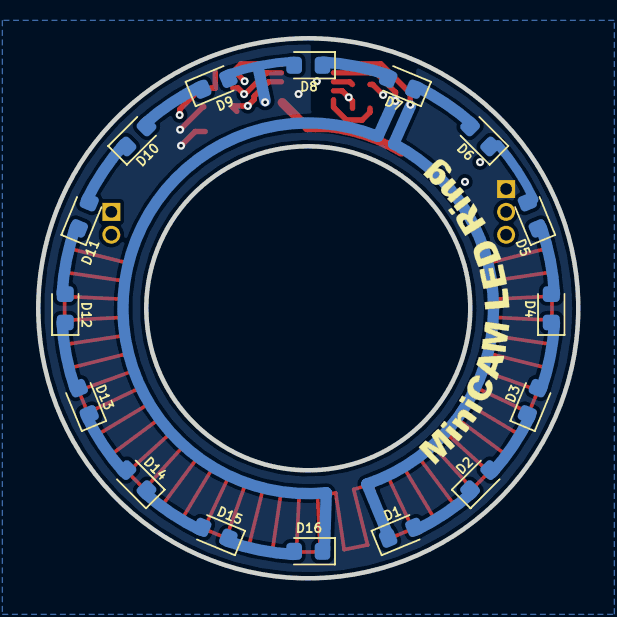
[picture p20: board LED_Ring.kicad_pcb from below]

Board: 4 copper layers, 30.0 x 30.0 mm, 27 parts (16 on the bottom side), 25 nets.

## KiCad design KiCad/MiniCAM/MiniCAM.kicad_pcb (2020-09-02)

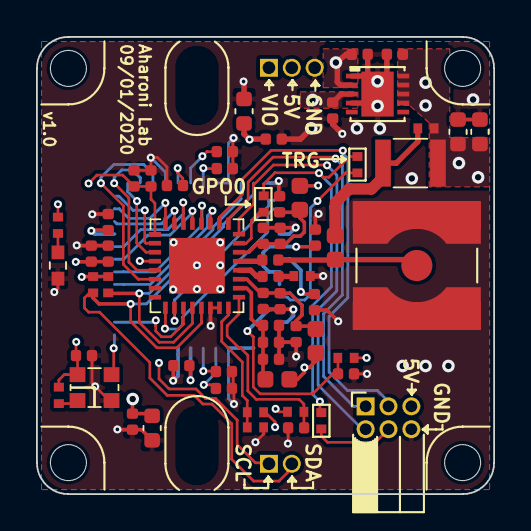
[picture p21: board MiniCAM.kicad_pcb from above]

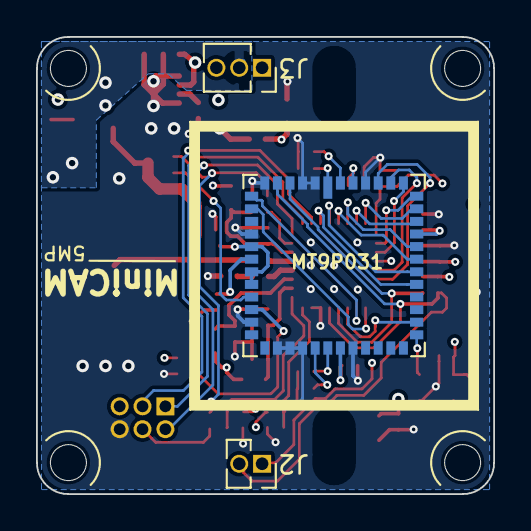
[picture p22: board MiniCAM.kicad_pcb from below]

Board: 4 copper layers, 25.4 x 25.4 mm, 69 parts (3 on the bottom side), 40 nets.

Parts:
C1, C2, C3, C11, C16, C33, C35: 1uF; C_0402_1005Metric_L
C4, C5, C6, C7, C8, C9, C10, C14, C15, C19, C22, C24, C27, C30, C32: 0.1uF; C_0402_1005Metric_L
C12, C13, C17, C36: 10uF; C_0603_1608Metric_L
C18, C21, C26, C29, C31, C34: 10nF; C_0402_1005Metric_L
C20, C23, C28: 4.7uF; C_0402_1005Metric_L
C25: 47nF; C_0402_1005Metric_L
D1: LED_Small_ALT; LED_SC80X160X65L40L
H1, H2, H3, H4, H5, H6: MountingHole; Conn_1x1_700_Circular_Pad
J1: SMA-J-P-H-RA-TH1; SMA_Amphenol_132134-10_Vertical
J2: Conn_01x02; PinSocket_1x02_P1.27mm_Vertical
J3: Conn_01x03; PinSocket_1x03_P1.27mm_Vertical
J4: Conn_02x03_Odd_Even; PinSocket_2x03_P1.27mm_Horizontal
L1, L3, L4, L5: BLM18PG471SN1D; L_0603_1608Metric_L
L2: ADL3225V-470MT-TL000; L_1210_3225Metric_L
R1, R5, R6: 2K; R_0402_1005Metric_ERJ_L
R2: 500; R_0402_1005Metric_ERJ_L
R3: 50; R_0402_1005Metric_ERJ_L
R4: 1K; R_0402_1005Metric_ERJ_L
R7, R8: 10K; R_0402_1005Metric_ERJ_L
R9: 100K; R_0402_1005Metric_ERJ_L
R10: DNL; R_0402_1005Metric_ERJ_L
R11, R12, R13: 0; R_0402_1005Metric_ERJ_L
U1: NCV8154MW180280TBG; DFN10_3x3_11P50_300X300X100L40X24T250X180N
U2: DS90UB933-Q1; QFN_33_P50_500X500X80L40X24T310L
U3: MT9P031; iLCC48P70_1000X1000X135L80X40N
U4: SiT_2.5mmx2mm; OSC_CC250X200X80L70X75L

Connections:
+1V8: C2.1, C14.1, C15.1, C16.1, C31.1, C32.1, C36.1, L3.1, L4.1, L5.1, R8.1, U1.2, U2.28, U3.12, U3.47
+2V8: C3.1, C4.1, C5.1, C6.1, C7.1, C8.1, C9.1, C10.1, C11.1, C17.1, C29.1, C30.1, C34.1, J3.1, R4.1, R5.1, R6.1, R7.1, R10.1, U1.3, U2.25, U3.1, U3.11, U3.13, U3.14, U3.23, U3.24, U3.25, U3.39, U3.48, U4.4
+5V: C1.1, C12.1, C13.1, J3.2, J4.5, L2.2, R1.1, R2.1, U1.7, U1.8, U1.9, U1.10
/COAX+: C24.2, J1.1, L1.1
/DIN0: U2.19, U3.35
/DIN1: U2.20, U3.36
/DIN2: U2.21, U3.37
/DIN3: U2.22, U3.38
/DIN4: U2.23, U3.40
/DIN5: U2.24, U3.41
/DIN6: U2.26, U3.42
/DIN7: U2.27, U3.43
/DIN8: U2.29, U3.44
/DIN9: U2.30, U3.45
/EXTCLK: U3.31, U4.3
/FV: U2.2, U3.7
/GPO0: R11.1, R12.1, R13.2
/GPO1: J4.2, U2.16
/GPO2: J4.1, U2.17
/GPO3: J4.3, U2.18
/LV: U2.1, U3.8
/MODE: R8.2, R9.1, U2.8
/PCLK: U2.3, U3.32
/PDB: C35.1, R7.2, U2.9
/SCL: J2.1, R6.2, U2.4, U3.4
/SDA: J2.2, R5.2, U2.5, U3.5
/TRIGGER: R11.2, U3.15
/VDDCML: C26.1, C27.1, C28.1, L5.2, U2.14
/VDDPLL: C21.1, C22.1, C23.1, L4.2, U2.10
/VDDT: C18.1, C19.1, C20.1, L3.2, U2.11
/nRESET: C33.1, R4.2, U3.16
GND: C1.2, C2.2, C3.2, C4.2, C5.2, C6.2, C7.2, C8.2, C9.2, C10.2, C11.2, C12.2, C13.2, C14.2, C15.2, C16.2, C17.2, C18.2, C19.2, C20.2, C21.2, C22.2, C23.2, C26.2, C27.2, C28.2, C29.2, C30.2, C31.2, C32.2, C33.2, C34.2, C35.2, C36.2, D1.1, J1.2, J3.3, J4.6, R3.2, R9.2, U1.1, U1.4, U1.11, U2.6, U2.7, U2.33, U3.2, U3.3, U3.6, U3.10, U3.17, U3.20, U3.21, U3.22, U3.26, U3.46, U4.2
unnamed: C24.1, U2.13
unnamed: C25.1, U2.12
unnamed: C25.2, R3.1
unnamed: D1.2, R2.2
unnamed: J4.4, R12.2
unnamed: L1.2, L2.1, R1.2
unnamed: R10.2, U4.1
unnamed: R13.1, U2.15

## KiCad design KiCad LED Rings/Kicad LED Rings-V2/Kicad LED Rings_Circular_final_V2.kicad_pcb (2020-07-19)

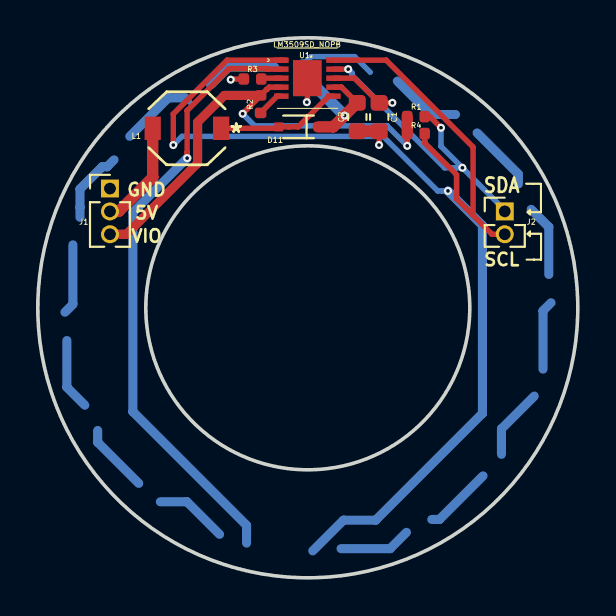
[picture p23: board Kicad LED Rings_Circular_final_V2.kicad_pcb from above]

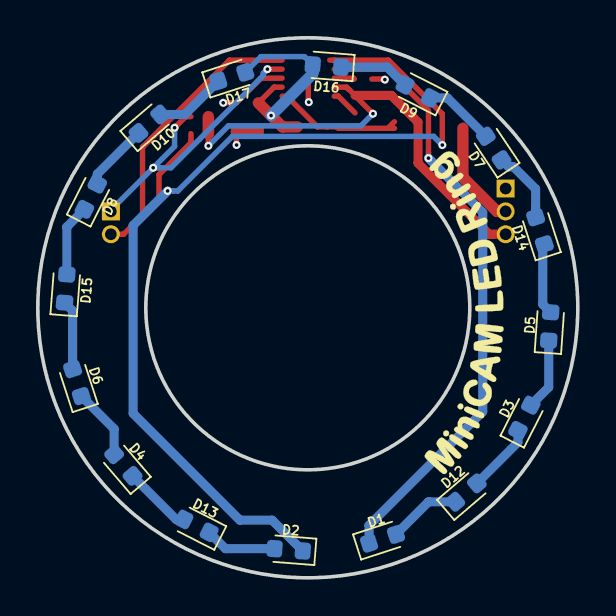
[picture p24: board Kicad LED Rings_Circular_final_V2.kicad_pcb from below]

Board: 4 copper layers, 30.0 x 30.0 mm, 27 parts (16 on the bottom side), 25 nets.

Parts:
C1: 1uF; C_0603_1608Metric
C2: 10uF; C_0603_1608Metric
D1, D2, D3, D4, D5, D6, D7, D8, D9, D10, D12, D13, D14, D15, D16, D17: LED_Small_ALT; LED_0603_1608Metric
D11: D_Schottky; SOD323(F)
J1: Conn_01x02_Female; PinHeader_1x03_P1.27mm_Vertical
J2: Conn_01x02_Male; PinHeader_1x02_P1.27mm_Vertical
L1: 10uH; VLF4012AT-100MR79
R1, R2, R4: 10K; R_0402_1005Metric
R3: 8K; R_0402_1005Metric
U1: LM3509SD_NOPB; LM3509SD&slash_NOPB

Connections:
+2V8: J1.3, R1.2, R2.1, R4.2, U1.4
+5V: C1.2, J1.2, L1.2, U1.8
GND: C1.1, C2.1, J1.1, R3.1, U1.11
unnamed: D1.1, U1.2
unnamed: D1.2, D12.1
unnamed: D2.1, U1.1
unnamed: D3.2, D5.1
unnamed: D4.2, D6.1
unnamed: D7.2, D9.1
unnamed: D8.2, D10.1
unnamed: D10.2, D17.1
unnamed: D11.2, L1.1, U1.6
unnamed: D3.1, D12.2
unnamed: D2.2, D13.1
unnamed: D4.1, D13.2
unnamed: D5.2, D14.1
unnamed: D7.1, D14.2
unnamed: D6.2, D15.1
unnamed: D8.1, D15.2
unnamed: D9.2, D16.1
unnamed: R2.2, U1.5
unnamed: R3.2, U1.3
OVP: C2.2, D11.1, D16.2, D17.2, U1.7
SCL: J2.2, R4.1, U1.10
SDA: J2.1, R1.1, U1.9

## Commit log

2020-07-17 Do initial schematic and import into pcb layout
    [MiniCAM.kicad_pcb, MiniCAM.sch]
2020-07-18 Finish initial schematic, layout, and routing.
    [MiniCAM.kicad_pcb, MiniCAM.sch]
2020-07-18 Switch 2 and 3 headers from pins to sockets. Generate STEP file.
    [MiniCAM.sch]
2020-07-18 Switch 2 and 3 socket headers for longer 3D model ones. Generate new STEP.
    [MiniCAM.kicad_pcb]
2020-07-19 Move LED ring headers to a consistent 4mm x 1mm spacing from center on lens.
    [MiniCAM.kicad_pcb, MiniCAM.sch]
2020-07-19 Added LED Ring PCB
    1. Made the led rings closer to outer edge;
    2. Added text for GND, 5V, VIO, SDA, and SCL;
    3. Added text MiniCAM LED Ring;
    4. Shfited the male pin headers to fit the female pin headers on Daniel's behavior camera pcb;
    5. made the center hole of led ring pcb bigger for bigger m12 lens holder.
    [10uH Inductor_VLF4012AT-100MR79 v2.step, DSC0010A.stp, Diode-Schottky-BAT760 v5.step, Kicad LED Rings.sch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]
2020-07-19 LED Ring PCB
    Roated the MiniCAM LED Ring by 90 degrees.
    [Kicad LED Rings_Circular_final.kicad_pcb, Kicad LED Rings_Circular_final_V2.kicad_pcb]
2020-07-20 Add connection to TRIG pin of sensor along with 0 resistors
    [MiniCAM.kicad_pcb, MiniCAM.sch]
2020-07-20 Forgot to save schematic for last commit. Here it is.
    [MiniCAM.sch]
2020-07-20 Updated LED ring pcb
    Changed Rset from 12k to 9.5k which can generate 25mA current for LEDs
    [Kicad LED Rings.sch]
2020-07-22 Generate BOM, PnP, Gerbers. Check and correct DRC errors. v0.1
    [MiniCAM-B_Cu.gbr, MiniCAM-B_Mask.gbr, MiniCAM-B_Paste.gbr, MiniCAM-B_SilkS.gbr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]
2020-07-30 Updated LED Ring PCB board
    updated BOM;
    updated Gerber;
    [Kicad LED Rings.sch, Kicad LED Rings_Circular_final-B_Cu.gbr, Kicad LED Rings_Circular_final-B_Mask.gbr, Kicad LED Rings_Circular_final-B_Paste.gbr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]
2020-07-30 Updated LED ring PCB
    added part NO. of LM3509SD_NOPB
    [Kicad LED Rings.sch, Kicad LED Rings_bom_.csv]
2020-07-30 Updated LED Ring PCB
    Changed '10uF 0603 25V' to '10uF 1210 50V'
    [Kicad LED Rings-B_Cu.gbr, Kicad LED Rings-B_Mask.gbr, Kicad LED Rings-B_Paste.gbr, Kicad LED Rings-B_SilkS.gbr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]
2020-07-30 Updated LED ring PCB Board
    Changed 10UF 0603 to 1210 50V: C1210C106K5RACTU
    [Kicad LED Rings_bom_.csv, MiniCAM-B_Cu.gbr, MiniCAM-B_Mask.gbr, MiniCAM-B_Paste.gbr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]
2020-07-30 Updated LED Ring PCB
2020-07-30 Updated LED ring PCB
    Added LED Ring PCB logo
    [Kicad LED Rings-B_Cu.gbr, Kicad LED Rings-B_Mask.gbr, Kicad LED Rings-B_Paste.gbr, Kicad LED Rings-B_SilkS.gbr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]
2020-07-31 Upldated LED ring PCB
    Changed 10uF Cout to C2012X5R1E225M125AC;
    Changed 10uH inductor to NRS4012T100MDGJ;
    [IND_TAIYO_NRS4012_TAY.step, Kicad LED Rings-B_Cu.gbr, Kicad LED Rings-B_Mask.gbr, Kicad LED Rings-B_Paste.gbr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]
2020-07-31 Updated LED ring PCB
    Removed the vias off the pads
    [Kicad LED Rings-B_Cu.gbr, Kicad LED Rings-B_Mask.gbr, Kicad LED Rings-B_Paste.gbr, Kicad LED Rings-B_SilkS.gbr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]
2020-08-01 Modified PCB layout
    [Kicad LED Rings.sch, LED_Ring.kicad_pcb]
2020-08-01 Change file naming. Generate GERBERS.
    [Kicad LED Rings.kicad_pcb, LED_Ring-B_Cu.gbr, LED_Ring-B_Mask.gbr, LED_Ring-B_Paste.gbr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]
2020-09-02 Correct minor error on top silk screen. Change to rev v1.0
    [MiniCAM-B_Cu.gbr, MiniCAM-B_Mask.gbr, MiniCAM-B_Paste.gbr, MiniCAM-B_SilkS.gbr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]
2020-09-02 updated led ring pcb board
    [LED_Ring.kicad_pcb, LED_Ring.sch]
2020-09-02 Updated LED ring pcb
    regenerated Gerber, position, and drl files
    [Kicad LED Rings-B_Cu.gbr, Kicad LED Rings-B_Mask.gbr, Kicad LED Rings-B_Paste.gbr, Kicad LED Rings-B_SilkS.gbr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]
2020-09-08 Update output files and check part numbers for v1.0 fabrication
    [Kicad LED Rings_bom_.csv, LED_Ring-B_Cu.gbr, LED_Ring-B_Mask.gbr, LED_Ring-B_Paste.gbr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]
2021-06-14 Update readme and add img and housing files
    [MiniCAM_5MP_Back_Housing.stl]
2021-06-25 Clean up MiniCAM KiCad schematic
    [MiniCAM.sch]

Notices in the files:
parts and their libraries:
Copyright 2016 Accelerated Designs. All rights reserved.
